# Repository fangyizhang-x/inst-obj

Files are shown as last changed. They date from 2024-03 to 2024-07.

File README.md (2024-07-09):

# Instrumented Objects for Assessing Compliant Robotic Grasping
Project page for the paper "Towards assessing compliant robotic grasping from first-object perspective via instrumented objects", published in the journal RA-L.
```
@ARTICLE{10538419,
  author={Knopke, Maceon and Zhu, Liguo and Corke, Peter and Zhang, Fangyi},
  journal={IEEE Robotics and Automation Letters}, 
  title={Towards Assessing Compliant Robotic Grasping From First-Object Perspective via Instrumented Objects}, 
  year={2024},
  volume={9},
  number={7},
  pages={6320-6327},
  keywords={Sensors;Faces;Magnetic sensors;Force;Magnets;Grasping;Three-dimensional displays;Grasping;methods and tools for robot system design;soft sensors and actuators},
  doi={10.1109/LRA.2024.3405371}}
```

Please refer to the paper via [IEEE](https://ieeexplore.ieee.org/document/10538419) or [arXiv](https://arxiv.org/abs/2312.14466) for more details.

Watch the video (https://www.youtube.com/watch?v=kQSZlNxYRrs)

For fabrication details, please refer to the [fabrication readme](Fabrication_Readme.md).

For the contact estimation, codes and data are in [Contact_Estimation](Contact_Estimation).

The full results for the other four faces can be seen in [detailed_results_for_the_other_four_faces.pdf](detailed_results_for_the_other_four_faces.pdf).

## Other Machine Learning Methods for Contact Estimation
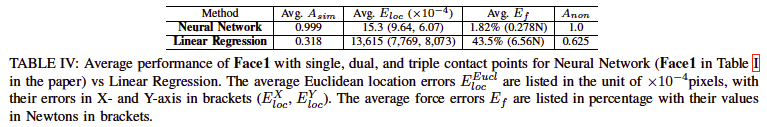
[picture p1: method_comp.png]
Neural Networks vs Linear Regression


A comparison was made to a baseline linear regression method, whose results are shown in the above table. The linear regression has very poor performance in all metrics, indicating it is not suitable for modeling such complex non-linear mapping from Hall-effect signals to contact forces. The fully-connected network used in this work is just a proof of concept for data-driven contact estimation via Hall-effect signals. We do not claim the optimality of the neural network used in the paper and it is worth exploring more appropriate machine learning methods for different observations in future works and all feasible solutions will help scale the application of instrumented compliant objects for robotic grasping performance assessment.

## Training Data Collection: Balancing the spatial and temporal coverage of training data
As discussed in Section VII, studies in Section V-E and Section V-F showed that the location coverage of training data is critical for better contact location/case estimation accuracy, while much less data (2683 samples in total, and about 19 samples for each contact location/case) can enable accurate contact force estimation. In future training/calibration data collection, a better balance can be achieved by collecting less data for each contact location/case but covering as many contact locations and numbers of contacts as possible.

## Other Designs
As introduced in the Introduction of the [paper](https://ieeexplore.ieee.org/document/10538419), this work is motivated to assess robotic grasping of compliant objects by measuring the stress or damage from a first-object perspective using mock objects (instrumented compliant objects). From a mock-compliant object perspective, the possibility of extending a design for different properties (such as hardness and shapes) and for providing different observations (such as contact force, deformation, and shape changes) is critical. Therefore, as a proof of concept, this paper adopts:
1) the Hall-sensor-based silicone design which can be adapted to different hardness and shapes and for observing 2D or 3D contact forces, deformation, and shape changes; and 
2) the machine learning approach which can model various input-output mappings if with required training data and unique input-output pairs.

However, as discussed in the [paper](https://ieeexplore.ieee.org/document/10538419), we do not claim the current design’s optimality. More designs are worth exploring in future works and all feasible designs (including variants of the work by Kıiva et al) will help to extend the application of instrumented objects for assessing the grasping of various compliant objects. If only 2D tactile pressure is needed, some off-the-shelf sensor films could be a good option, such as a tactile pressure indicating sensor film (https://www.sensorprod.com/index.php).

## Control of the Object's Hardness
As discussed in Section IV in the [paper](https://ieeexplore.ieee.org/document/10538419), if more or less deformation is needed, different properties including the hardness of the instrumented object can be achieved by using different materials such as silicone with different levels of hardness for the outer shell. By adjusting this hardness, the deformation measured by the sensors can be tailored to match specific scenarios. The Shore hardness scale ranges from soft rubbers and gels (Shore 00), soft to semi-rigid rubbers (Shore A) and hard rubbers/plastics (Shore D). In this paper, all experiments utilized a shell made from Platsil GEL-10 Prosthetic Grade Silicone, which has a Shore hardness of A10. Shore A10 was chosen because it provides firmness, simplifying prototype design and testing, while still allowing elastic deformation under reasonable force (e.g., pinching or firm pressing). This hardness can produce deformation for detecting as little as 0.12N contact force changes. Switching to a silicone with lower Shore hardness (e.g., Shore 0010-0030) is expected to increase sensitivity, but would result in a lower readable maximum force. Increasing the hardness would decrease the sensitivity, while allowing for a higher range of applied force. Conversely, increasing hardness too much into the mid Shore D range could lead to inaccurate readings due to deformation of the plastic inner core and PCBs. 

While silicone is suggested due to its elastic properties and ease of use, alternative elastomers could also be used, such as Thermoplastic Polyurethane (TPU), which can be 3D printed using FDM and SLS technologies. TPU offers a large hardness range, commonly measured at Shore 60A-90A, although some variants can be as low as Shore 0030. Elastic resins are also available for resin 3D printers, with a hardness of around Shore 50-80A.

## Limitations and Future Outlook
The current design generally worked well in contact estimation, although there were some design drawbacks that caused non-trivial performance degradation with simultaneous contacts from multiple faces and the internal core shifting w.r.t. the silicone shell between calibration and evaluation.

This concept and design can be extended in the future for more comprehensive measurements of compliant robotic grasping (such as the measurement of 3D contact force and more simultaneous contact points, and the estimation of deformation and shape changes) with various robotic grippers (such as anthropomorphic robotic hands and soft robotic grippers/hands). Ultimately this could lead to a robust framework for autonomously generating designs of instrumented objects with various measurement capabilities and physical properties (shapes, sizes, stiffness, etc) for benchmark purposes. Such instrumented objects could close the loop of developing/learning solutions for different compliant robotic manipulation tasks by providing timely and accurate feedback from a first-object perspective.

### Use for assessing soft robotic grippers/hands
To be used for assessing soft robotic grippers/hands, the design might need to be adjusted in three aspects:
- collecting additional training data to cover more complicated contact situations with the object,
- denser sensors or more effective sensor layouts for detecting more complicated contacts (e.g., large contact areas that cover many more than three pixels), and
- a softer outer shell to be more sensitive to subtle deformations (depending on how compliant the grippers/hands are).

### Use for assessing grasping by anthropomorphic robotic hands
This instrumented object can be extended for assessing grasping by anthropomorphic robotic hands, but needs additional training data to cover situations different from the three types of probes currently used for training data collection. For better and stabler performance, the current design also needs to be optimized to eliminate the Problems a) and b) discussed in Section VII in the [paper](https://ieeexplore.ieee.org/document/10538419).

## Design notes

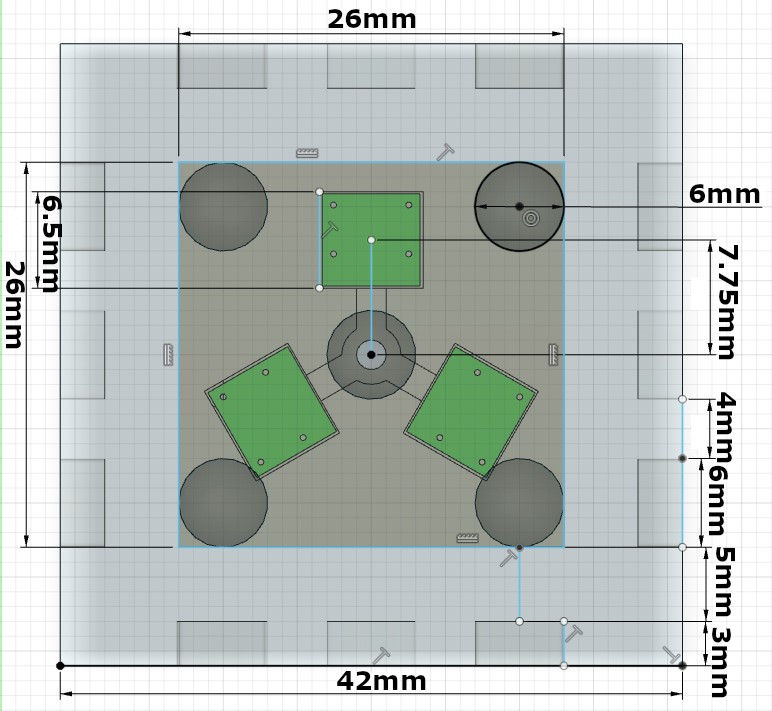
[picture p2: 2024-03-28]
Images/sensor_positions+dimensions_v4.jpg

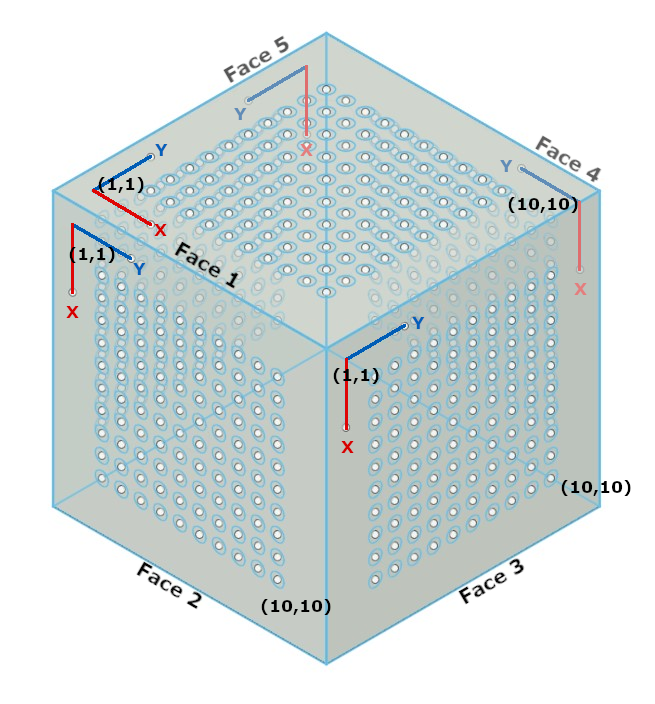
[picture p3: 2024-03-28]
Images/3D faces_V3.png

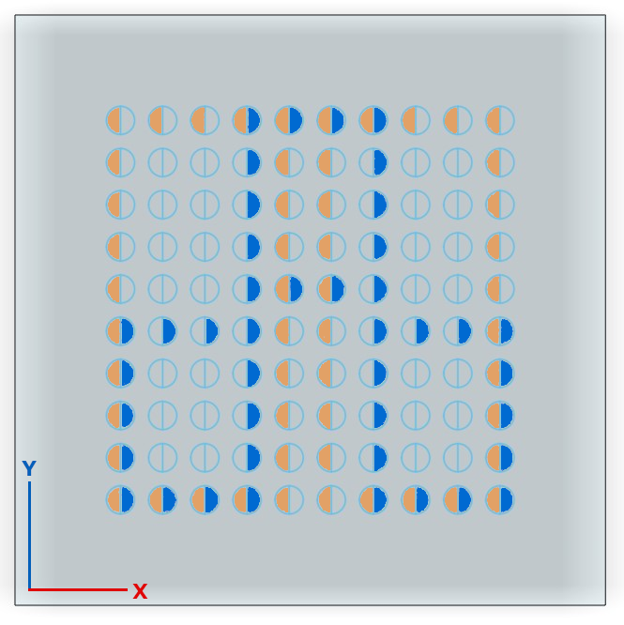
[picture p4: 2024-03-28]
Images/grid2 - coloured_V2.png

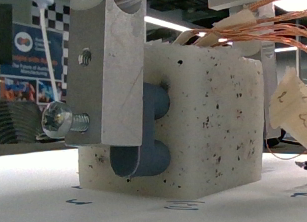
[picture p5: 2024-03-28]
Images/f2-t2-d1-2.png

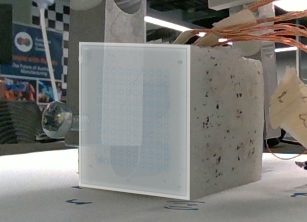
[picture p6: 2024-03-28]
Images/f2-t2-d1-2-Overlay.png

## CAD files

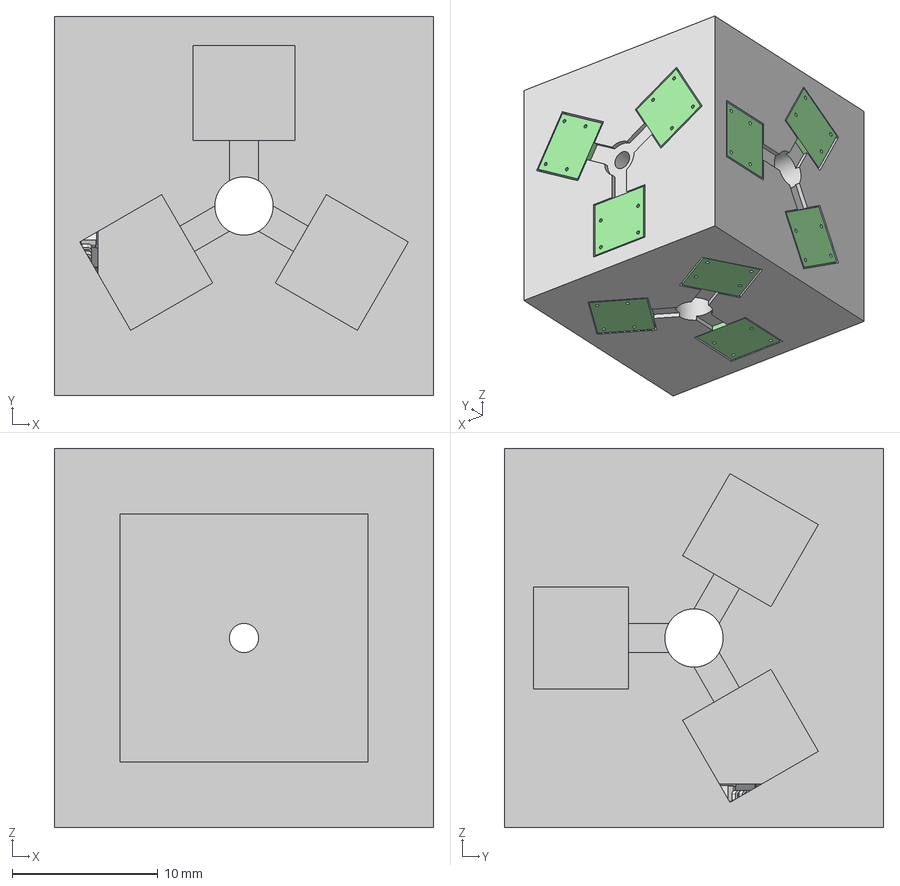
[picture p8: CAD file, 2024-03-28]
CAD_Models/Internal_multi_sensor_core.step
26.0 x 26.0 x 26.0 mm
_autosave-TMAG5273A1_PCB_mini PCB x 9

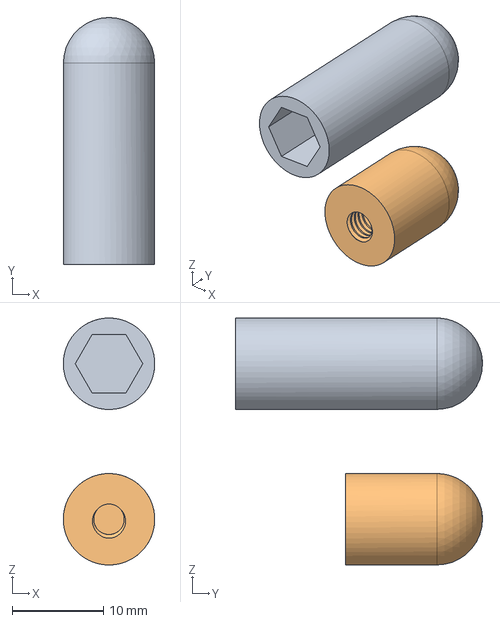
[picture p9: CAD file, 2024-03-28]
CAD_Models/probe_1.step
10.00 x 27.0 x 27.0 mm

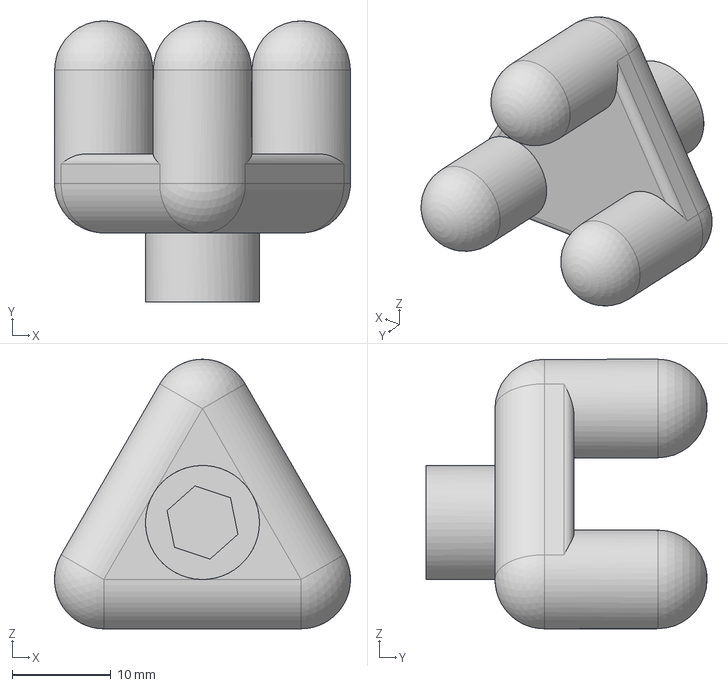
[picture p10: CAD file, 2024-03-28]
CAD_Models/Probe_3.step
30.0 x 28.5 x 27.3 mm

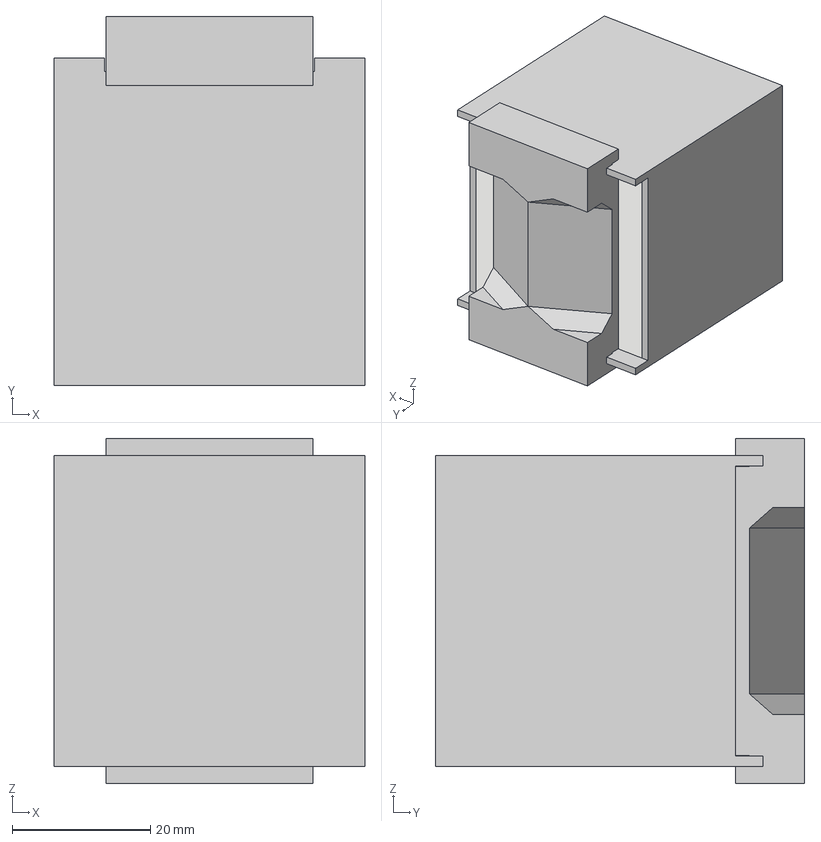
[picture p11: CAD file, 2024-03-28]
CAD_Models/Internal_3_hall_mould.step
45.0 x 53.5 x 50.0 mm

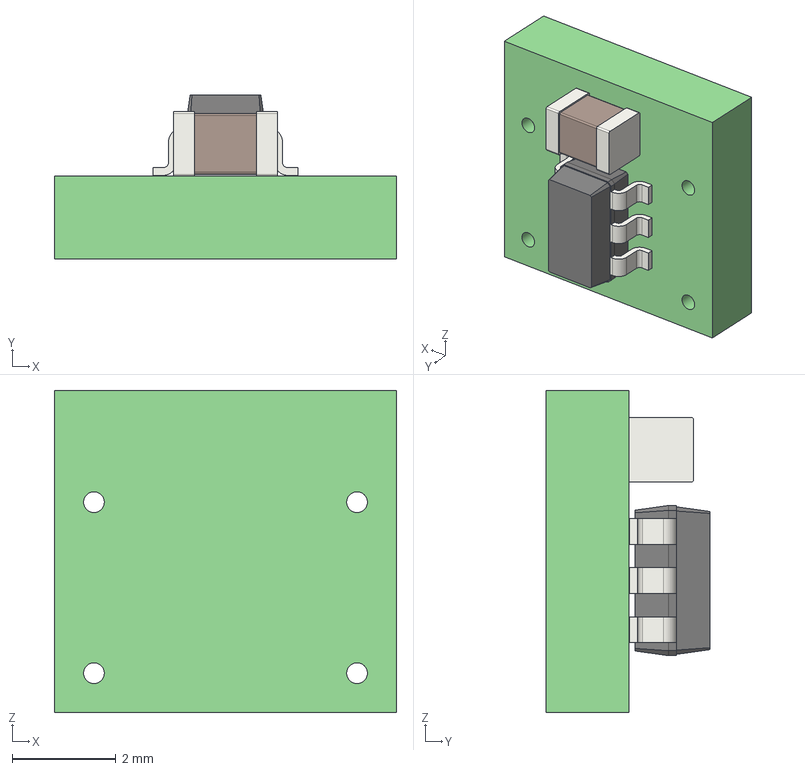
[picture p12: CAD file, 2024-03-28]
CAD_Models/TMAG5273A1_PCB_mini.step
6.60 x 3.16 x 6.22 mm
_autosave-TMAG5273A1_PCB_mini PCB

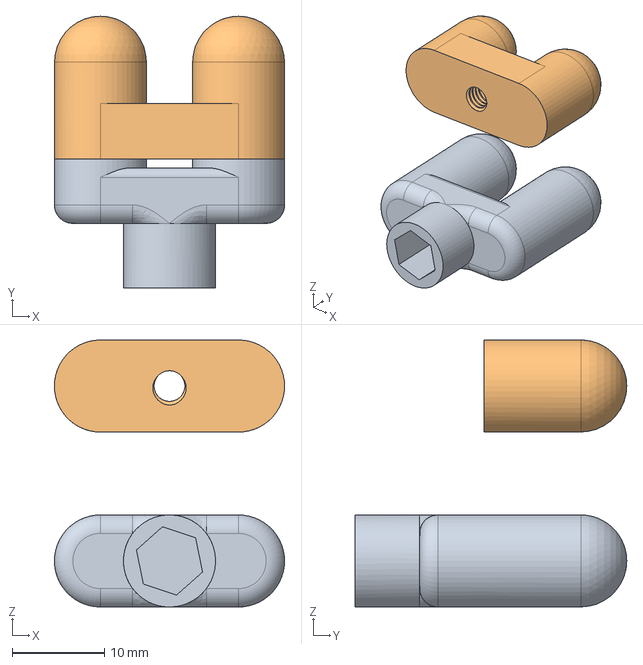
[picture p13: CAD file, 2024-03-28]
CAD_Models/Probe_2.step
25.0 x 29.5 x 29.0 mm

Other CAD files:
CAD_Models/Internal_3_hall_mould.f3d
CAD_Models/Internal_multi_sensor_core.f3d
CAD_Models/Probe_2.f3d
CAD_Models/Probe_3.f3d
CAD_Models/TMAG5273A1_PCB_mini.f3d
CAD_Models/probe_1.f3d

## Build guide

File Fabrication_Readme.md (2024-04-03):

# Fabrication Readme

A prototype instrumented object is shown in Fig. 3 in the paper (https://arxiv.org/abs/2312.14466). 

- The first fabrication step of this prototype involves assembling the internal sensor core (Fig. 3a). This core consists of a rigid cube, 3D printed from PETG filament, which offers good layer adhesion and durability. The cube has a hollow centre designed for wiring purposes. On each face of the cube, three TMAG5273 Hall sensors are securely glued into recesses. These sensors are evenly spaced around the middle of the face, where the connected signal and power wires are routed into the centre of the cube.

- Each of the sensors is secured on a small custom PCB with a power decoupling capacitor, and is connected to the Arduino microcontroller’s SDA, SCL and GND pins via thin 0.25mm enamel copper wires. For prototyping, the Arduino was mounted outside of the prototype due to space and wiring constraints, which prevented the use of one of the six faces of the prototype -- 21 wires are required in total for connecting the sensors on the other five faces to the microcontroller and one face is used for passing these wires. In a complete implementation, an internal wireless microcontroller can be used together with a battery to eliminate the dependency on external wires.

- The silicone shell (Fig. 3b) was moulded using a 2-part, 3D-printed mould. The outer mould was a large cube with 6mm diameter extrusions at each magnet location, while the inner mould was a cube of the same size as the internal sensor core. Platsil GEL-10 Prosthetic Grade Silicone was used in this paper to create the silicone shell with a desirable hardness of Shore A10. Different properties of the instrumented objects can be achieved by using different materials such as silicone with different levels of hardness. Once cured, the mould was separated, and the silicone shell was peeled out. The internal core was then pushed into the shell to add rigidity.

- To complete the assembly, the magnets were inserted into each of their moulded holes on the outside of the shell with the north poles facing outward. A thin layer of additional silicone was then applied to the surface, sealing the magnets in place as in Fig. 3b.

## CAD_Models:
- The file Internal_3_hall_mould contains the two part mould required to create the silicone shell of the sensor. These two parts clip together and mixed 2-part/platinum cure silicone can be poured in. It is recommended to place the filled mould in a vacuum chamber to remove bubbles from within the silicone during the curing process. 

-  The file Internal_multi_sensor_core is the core which is inserted into the shell. The supplied pcb design fits into the surface of the core and attached wires are routed into the center of each face and through the core.

- The files Probe_x contain the probes used during data collection for the paper. These were mounted onto a vernier dual force sensor during initial calibration and onto a Franka Emika Gripper for Panda for data collection.

- The file TMAG5273A1_PCB_mini is a cad model of the PCB and attached TMAG5273A1 hall effect sensor and capacitor. 

## PCB:
The supplied pcb can be opened using kicad for editing. This pcb holds a single TMAG5273A1 sensor and capacitor. Wires are inserted into the through holes and soldered. Reommend gluing the fibers to the pcb for strain relief. The folder GBR_Files contains the files required for printing via PCBway.

## Images:
Various images from the paper and some extas are supplied to demonstrate the assembly and testing setups used.

## Arduino Code:
The code provided was used in multiple experiments, it is set up to program and read data from a 3 sensor prototype, and a 15 sensor prototype. It runs on an arduino mega and can be connected to a cnc machine that accepts grbl to control the probes if required. Data from the sensors is printed over serial and putty was used to save the large amounts of incoming data.

## Notes:
If further information is required please contact fangyi.zhang@qut.edu.au and a more detailed guideline can be created.

The current design can be improved upon by switching to a sensor that remembers programmed i2c addresses. The TMAG5273A1 only has 4 factory addresses and new addresses must be assigned on startup to use multiple simultaneously. This required an additional power wire to power on each sensor individually during startup for programming. Using a sensor that recalls its programmed address on boot will simplify the wiring significantly. Other methods could be the use of multiplexers or alternative communication protocols. If the number of required GPIO is reduced an internal microcontroller with wireless capability can be used such as an esp32s3.

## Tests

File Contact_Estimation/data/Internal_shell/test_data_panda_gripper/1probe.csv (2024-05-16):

Time | Left | Right-blue | F5-X1 | F5-Y1 | F5-Z1 | F5-X2 | F5-Y2 | F5-Z2 | F5-X3 | F5-Y3 | F5-Z3 | F3-X1 | F3-Y1 | F3-Z1 | F3-X2 | F3-Y2 | F3-Z2 | F3-X3 | F3-Y3 | F3-Z3 | F1-X1 | F1-Y1 | F1-Z1 | F1-X2 | F1-Y2 | F1-Z2 | F1-X3 | F1-Y3 | F1-Z3 | F2-X1 | F2-Y1 | F2-Z1 | F2-X2 | F2-Y2 | F2-Z2 | F2-X3 | F2-Y3 | F2-Z3 | F4-X1 | F4-Y1 | F4-Z1 | F4-X2 | F4-Y2 | F4-Z2 | F4-X3 | F4-Y3 | F4-Z3 | Probe_Face_1 | Probe_Pos_1 | Probe_Face_2 | Probe_Pos_2
1690355952 | 0.09 | 0.32 | 397 | 125 | 1129 | -233 | 817 | 1275 | 163 | -985 | -1041 | 1567 | -196 | -492 | 124 | -2412 | -369 | -1527 | -590 | -552 | 1702 | 795 | -88 | -995 | 212 | 241 | -1387 | -161 | -157 | 566 | -2592 | -94 | -417 | 412 | 437 | 615 | 517 | 775 | 144 | -427 | -252 | 420 | -1292 | -978 | 1907 | 796 | 248 | 3 | 54 | 5 | 44
1690355952 | 0.09 | 0.32 | 403 | 91 | 1100 | -205 | 745 | 1285 | 182 | -1052 | -1039 | 1615 | -212 | -472 | 93 | -2391 | -341 | -1544 | -554 | -578 | 1731 | 790 | -106 | -1061 | 191 | 224 | -1453 | -196 | -150 | 555 | -2589 | -89 | -433 | 400 | 448 | 635 | 480 | 744 | 80 | -440 | -245 | 438 | -1246 | -975 | 1846 | 791 | 228 | 3 | 54 | 5 | 44
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

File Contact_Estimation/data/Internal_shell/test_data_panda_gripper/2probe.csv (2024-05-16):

Time | Left | Right-blue | F5-X1 | F5-Y1 | F5-Z1 | F5-X2 | F5-Y2 | F5-Z2 | F5-X3 | F5-Y3 | F5-Z3 | F3-X1 | F3-Y1 | F3-Z1 | F3-X2 | F3-Y2 | F3-Z2 | F3-X3 | F3-Y3 | F3-Z3 | F1-X1 | F1-Y1 | F1-Z1 | F1-X2 | F1-Y2 | F1-Z2 | F1-X3 | F1-Y3 | F1-Z3 | F2-X1 | F2-Y1 | F2-Z1 | F2-X2 | F2-Y2 | F2-Z2 | F2-X3 | F2-Y3 | F2-Z3 | F4-X1 | F4-Y1 | F4-Z1 | F4-X2 | F4-Y2 | F4-Z2 | F4-X3 | F4-Y3 | F4-Z3 | Probe_Face_1 | Probe_Pos_1 | Probe_Pos_2 | Probe_Face_2 | Probe_Pos_1 | Probe_Pos_2
1690358254 | 0.22 | 0.26 | 402 | 200 | 1252 | -217 | 975 | 1610 | 184 | -1079 | -1044 | 1439 | -167 | -466 | 196 | -2485 | -244 | -1552 | -441 | -603 | 1637 | 737 | -89 | -958 | 180 | 278 | -1428 | -96 | -169 | 264 | 64 | 130 | -465 | 467 | 506 | 395 | 494 | 610 | 74 | -452 | -233 | 412 | -1472 | -1134 |  |  |  | 3 | 35 | 86 | 5 | 38 | 83
1690358254 | 0.22 | 0.25 | 447 | 208 | 1263 | -225 | 965 | 1620 | 164 | -1059 | -1070 | 1467 | -191 | -451 | 202 | -2445 | -257 | -1603 | -416 | -604 | 1652 | 754 | -87 | -987 | 238 | 264 | -1410 | -90 | -187 | 272 | 129 | 129 | -459 | 417 | 513 | 405 | 465 | 623 | 82 | -444 | -259 | 427 | -1473 | -1115 |  |  |  | 3 | 35 | 86 | 5 | 38 | 83
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

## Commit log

2024-03-28 final version upload
    [External_sensor_schematic.kicad_pcb, External_sensor_schematic.kicad_sch, Internal_3_hall_mould.f3d, Internal_3_hall_mould.step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]
2024-05-16 Added data for contact estimation and updated readme.
    [1probe.csv, 2probe.csv, 3probe.csv]
